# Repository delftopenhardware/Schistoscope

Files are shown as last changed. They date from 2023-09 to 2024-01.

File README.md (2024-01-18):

# Schistoscope
TU Delft Open Hardware Schistoscope

Navigate to 'Assembly Guide' or https://delftopenhardware.github.io/SchistoscopeDocs/ to see how to build the scope

All the parts CAD parts are located in the 'CAD' folder

The BOM can be found in the 'BOM' folder    



This project is a part of the Inspired  
https://inspired-diagnostics.info/

## Reference 
Oyibo, P., Jujjavarapu, S., Meulah, B., Agbana, T., Braakman, I., Van Diepen, A., Bengtson, M., Van Lieshout, L., Oyibo, W., Vdovine, G., & Diehl, J. C. (2022). Schistoscope: An Automated Microscope with Artificial Intelligence for Detection of Schistosoma haematobium Eggs in Resource-Limited Settings. Micromachines, 13(5), 643. https://doi.org/10.3390/mi13050643

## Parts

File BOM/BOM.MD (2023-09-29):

| Item # | Name | Specs. | Qty. | Price per piece (€) | Shipping (€) | Total   per Schistoscope (€) |  | Total cost (€) |  €    799,23  | Link |  |  |
|---|---|---|---|---|---|---|---|---|---|---|---|---|
| Motors   and drivers |  |   |   |   |   |   |   |   |   |   |  |  |
| 1 | Stepper motor | NEMA 11, 1 mm pitch, 50 mm | 2 |  €                     24,59  |  €         24,20  |  €                                   73,38  |   |   |   | https://nl.aliexpress.com/item/1005005533260185.html?spm=a2g0o.productlist.main.21.d7193af5nTc0bL&algo_pvid=0311f4ec-5321-4d68-99e3-2e47c6b58b74&algo_exp_id=0311f4ec-5321-4d68-99e3-2e47c6b58b74-10&pdp_npi=4%40dis%21EUR%2136.33%2135.24%21%21%2138.24%21%21%40211b88ef16938677846513431e329a%2112000033439717476%21sea%21NL%210%21A&curPageLogUid=17Ds95Ps0tr9 |  |  |
| 2 | Stepper motor | NEMA 11, 1 mm pitch, 100 mm | 1 |  €                     25,10  |  €           5,61  |  €                                   30,71  |   |   |   | https://nl.aliexpress.com/item/1005005533260185.html?spm=a2g0o.productlist.main.21.d7193af5nTc0bL&algo_pvid=0311f4ec-5321-4d68-99e3-2e47c6b58b74&algo_exp_id=0311f4ec-5321-4d68-99e3-2e47c6b58b74-10&pdp_npi=4%40dis%21EUR%2136.33%2135.24%21%21%2138.24%21%21%40211b88ef16938677846513431e329a%2112000033439717476%21sea%21NL%210%21A&curPageLogUid=17Ds95Ps0tr9 |  |  |
| 3 | Stepper motor driver | DRV8825 + heatsink | 3 |  €                       1,05  |  €           1,55  |  €                                     4,70  |   |   |   | https://nl.aliexpress.com/item/1005001621676770.html?spm=a2g0o.productlist.main.45.7d113e71c5rpfz&algo_pvid=0ba04a30-e339-455d-b8e5-7db9d5e80bba&algo_exp_id=0ba04a30-e339-455d-b8e5-7db9d5e80bba-22&pdp_npi=4%40dis%21EUR%210.91%210.73%21%21%210.96%21%21%40211b88ee16938682042218596e4ee1%2112000020026811115%21sea%21NL%210%21A&curPageLogUid=FATsjuqZyCN2 |  |  |
|  |   |  |   |  |   |  |  |  |  |  |  |  |
| Structural   components |  |   |   |   |   |   |   |   |   |   |  |  |
| 5 | Aluminum profile | 20x20x350 mm | 2 |  €                       6,11  |  €           1,74  |  €                                   13,96  |   |   |   | https://nl.aliexpress.com/item/1005002537611699.html?spm=a2g0o.productlist.main.3.4a031ab0olaA8Y&algo_pvid=1cb8bec3-2328-4782-988c-cffaef372e91&algo_exp_id=1cb8bec3-2328-4782-988c-cffaef372e91-1&pdp_npi=4%40dis%21EUR%217.49%215.98%21%21%217.88%21%21%40211b88f016938699631611766e6877%2112000021048744254%21sea%21NL%210%21A&curPageLogUid=FJZzS7E2CY5k |  |  |
| 6 | Aluminum profile | 40x20x300 mm | 1 |  €                     11,87  |  €                -    |  €                                   11,87  |   |   |   | https://nl.aliexpress.com/item/1005002453496457.html?spm=a2g0o.productlist.main.51.1df46917MQxx1B&algo_pvid=2cc73904-420a-4249-9133-c5c1c338129d&algo_exp_id=2cc73904-420a-4249-9133-c5c1c338129d-25&pdp_npi=4%40dis%21EUR%2119.64%2119.64%21%21%2120.67%21%21%4021038eda16938702597077618e5c7a%2112000020710616520%21sea%21NL%210%21A&curPageLogUid=VMwzInqvGpVO |  |  |
| 7 | Aluminum profile | 20x20x300 mm | 3 |  €                       7,28  |  €           1,74  |  €                                   23,58  |   |   |   | https://nl.aliexpress.com/item/1005002537611699.html?spm=a2g0o.productlist.main.3.4a031ab0olaA8Y&algo_pvid=1cb8bec3-2328-4782-988c-cffaef372e91&algo_exp_id=1cb8bec3-2328-4782-988c-cffaef372e91-1&pdp_npi=4%40dis%21EUR%217.49%215.98%21%21%217.88%21%21%40211b88f016938699631611766e6877%2112000021048744254%21sea%21NL%210%21A&curPageLogUid=FJZzS7E2CY5k |  |  |
| 8 | Aluminum profile | 20x20x215 mm | 2 |  €                       8,46  |  €           1,74  |  €                                   18,66  |   |   |   | https://nl.aliexpress.com/item/1005002537611699.html?spm=a2g0o.productlist.main.3.4a031ab0olaA8Y&algo_pvid=1cb8bec3-2328-4782-988c-cffaef372e91&algo_exp_id=1cb8bec3-2328-4782-988c-cffaef372e91-1&pdp_npi=4%40dis%21EUR%217.49%215.98%21%21%217.88%21%21%40211b88f016938699631611766e6877%2112000021048744254%21sea%21NL%210%21A&curPageLogUid=FJZzS7E2CY5k |  |  |
| 9 | Aluminum profile | 20x20x200 mm | 2 |  €                       7,63  |  €           1,74  |  €                                   17,00  |   |   |   | https://nl.aliexpress.com/item/1005002537611699.html?spm=a2g0o.productlist.main.3.4a031ab0olaA8Y&algo_pvid=1cb8bec3-2328-4782-988c-cffaef372e91&algo_exp_id=1cb8bec3-2328-4782-988c-cffaef372e91-1&pdp_npi=4%40dis%21EUR%217.49%215.98%21%21%217.88%21%21%40211b88f016938699631611766e6877%2112000021048744254%21sea%21NL%210%21A&curPageLogUid=FJZzS7E2CY5k |  |  |
| 10 | Aluminum profile | 20x20x175 mm | 2 |  €                       7,63  |  €           1,74  |  €                                   17,00  |   |   |   | https://nl.aliexpress.com/item/1005002537611699.html?spm=a2g0o.productlist.main.3.4a031ab0olaA8Y&algo_pvid=1cb8bec3-2328-4782-988c-cffaef372e91&algo_exp_id=1cb8bec3-2328-4782-988c-cffaef372e91-1&pdp_npi=4%40dis%21EUR%217.49%215.98%21%21%217.88%21%21%40211b88f016938699631611766e6877%2112000021048744254%21sea%21NL%210%21A&curPageLogUid=FJZzS7E2CY5k |  |  |
| 11 | Corner brackets |   | 16 |  €                       6,46  |  €                -    |  €                                     6,46  |   |   |   | https://nl.aliexpress.com/item/4000063076132.html?spm=a2g0o.productlist.main.25.7da814435etbcl&algo_pvid=19aa6fcc-ced3-47ff-abb9-b12fac77b6bf&algo_exp_id=19aa6fcc-ced3-47ff-abb9-b12fac77b6bf-12&pdp_npi=4%40dis%21EUR%2112.20%216.46%21%21%2112.80%21%21%40211b615316947241743964861eaa47%2110000000161993707%21sea%21NL%210%21AS&curPageLogUid=rLXXE8yB8w6T |  |  |
| 12 | Rubber feet | M4 | 4 |  €                       3,68  |  €           4,96  |  €                                     8,64  |   |   |   | https://nl.aliexpress.com/item/1005003681572582.html?spm=a2g0o.productlist.main.25.5ca63b58zzCfgb&algo_pvid=e28b779e-7411-432f-84bb-55b8b368539a&algo_exp_id=e28b779e-7411-432f-84bb-55b8b368539a-12&pdp_npi=4%40dis%21EUR%214.71%214.61%21%21%214.94%21%21%40211b615316947243129446972eaa47%2112000026782305036%21sea%21NL%210%21AS&curPageLogUid=B0LszgvKN7rm |  |  |
| 13 | Spring | M5*15 mm | 4 |  €                       0,43  |  €           1,37  |  €                                     3,07  |   |   |   | https://nl.aliexpress.com/item/1005005974742507.html?spm=a2g0o.productlist.main.45.7bac5dd5iFG5OJ&algo_pvid=2046b9d0-bc3c-4736-8237-c5244236c177&algo_exp_id=2046b9d0-bc3c-4736-8237-c5244236c177-22&pdp_npi=4%40dis%21EUR%212.12%211.7%21%21%2116.27%21%21%40211b617a16939507018131128e6a33%2112000035130817674%21sea%21NL%210%21A&curPageLogUid=S3SDvNti9Aof |  |  |
| 14 | Hinge |  | 2 |  €                       0,23  |  €                -    |  €                                     0,46  |  |  |  | https://nl.aliexpress.com/item/32953581270.html?spm=a2g0o.productlist.main.5.6b3668aaplRnSN&algo_pvid=2c0c1b08-6c85-4129-bd1b-7743bc25a72d&algo_exp_id=2c0c1b08-6c85-4129-bd1b-7743bc25a72d-2&pdp_npi=4%40dis%21EUR%212.94%210.46%21%21%213.10%21%21%40211b617a16939508408492869e6a33%2166382201404%21sea%21NL%210%21A&curPageLogUid=eFfJ6r2JXGj9 |  |  |
| 15 | Lock plate |  | 1 |  €                       0,46  |  €                -    |  €                                     0,46  |  |  |  | https://nl.aliexpress.com/item/32933924674.html?spm=a2g0o.productlist.main.3.412c3931eQBrTb&algo_pvid=9e3379fe-aa2c-4b70-85b0-87a244084bad&algo_exp_id=9e3379fe-aa2c-4b70-85b0-87a244084bad-1&pdp_npi=4%40dis%21EUR%210.70%210.46%21%21%210.74%21%21%40211b617a16939509787254501e6a33%2166224476012%21sea%21NL%210%21A&curPageLogUid=FMX9X8mry7T9 |  |  |
|  |   |  |   |  |   |  |  |  |  |  |  |  |
| Mechanical   fasteners |  |   |   |   |   |   |   |   |   |   |  |  |
| 16 | Bolt | M2*6 mm | 8 |  €                       1,84  |  €                -    |  €                                     1,84  |   |   |   | https://nl.aliexpress.com/item/1005004833515587.html?spm=a2g0o.productlist.main.7.107a4abed7Lp4O&algo_pvid=4e5c6b8d-3b2b-4882-8919-a36d85c2f3a4&algo_exp_id=4e5c6b8d-3b2b-4882-8919-a36d85c2f3a4-3&pdp_npi=4%40dis%21EUR%2113.46%211.84%21%21%2114.12%21%21%40211b88f116947270870846250efcfc%2112000030659841609%21sea%21NL%210%21AS&curPageLogUid=aU9x01JDrid9 |  |  |
| 17 | Bolt | M2*8 mm | 12 |  |  |  |   |   |   |  |  |  |
| 18 | Bolt  | M2*10 mm | 8 |  |  |  |   |   |   |  |  |  |
| 19 | Bolt | M2*16 mm | 2 |  |  |  |   |   |   |  |  |  |
| 20 | Bolt | M3*6 mm | 2 |  €                       5,75  |  €                -    |  €                                     5,75  |  |  |  | https://nl.aliexpress.com/item/1005004833515587.html?spm=a2g0o.productlist.main.7.107a4abed7Lp4O&algo_pvid=4e5c6b8d-3b2b-4882-8919-a36d85c2f3a4&algo_exp_id=4e5c6b8d-3b2b-4882-8919-a36d85c2f3a4-3&pdp_npi=4%40dis%21EUR%2113.46%211.84%21%21%2114.12%21%21%40211b88f116947270870846250efcfc%2112000030659841609%21sea%21NL%210%21AS&curPageLogUid=aU9x01JDrid9 |  |  |
| 21 | Bolt | M3*8 mm | 19 |  |  |  |  |  |  |  |  |  |
| 22 | Bolt | M3*12 mm | 10 |  |  |  |  |  |  |  |  |  |
| 23 | Bolt | M3*16 mm \| countersunk | 12 |  |  |  |  |  |  |  |  |  |
| 24 | Bolt | M3*20 mm | 4 |  |  |  |  |  |  |  |  |  |
| 25 | Bolt | M4*8 mm | 98 |  €                       6,29  |  €                -    |  €                                     6,29  |  |  |  | https://nl.aliexpress.com/item/32879751148.html?spm=a2g0o.productlist.main.83.b89572a1z7If2W&algo_pvid=83133542-d8ce-405e-b2ad-da25d44a70e7&algo_exp_id=83133542-d8ce-405e-b2ad-da25d44a70e7-41&pdp_npi=4%40dis%21EUR%216.93%216.86%21%21%217.27%21%21%4021038eda16947280350625746e14c3%2165522335530%21sea%21NL%210%21AS&curPageLogUid=AfVsvWcOz8tB |  |  |
| 26 | Bolt | M4*12 mm | 4 |  €                       6,48  |  €                -    |  €                                     6,48  |  |  |  | https://nl.aliexpress.com/item/1005004129378778.html?spm=a2g0o.productlist.main.67.565d590atXPBRa&algo_pvid=966ad033-4291-4696-85c4-f2033d81a041&algo_exp_id=966ad033-4291-4696-85c4-f2033d81a041-33&pdp_npi=4%40dis%21EUR%2112.58%213.99%21%21%2113.19%21%21%4021038eda16947278400843976e14c3%2112000028131816313%21sea%21NL%210%21AS&curPageLogUid=WjhHm1uIKRo7 |  |  |
| 27 | Bolt  | M4*24 mm | 2 |  |  |  |  |  |  |  |  |  |
| 28 | Bolt | M4*60 mm | 3 |  €                       8,81  |  €                -    |  €                                     8,81  |  |  |  | https://nl.aliexpress.com/item/1005006034026066.html?spm=a2g0o.productlist.main.21.50886603JV22ri&algo_pvid=5ac0b68b-b2eb-4c67-9b40-9e0facd0099b&algo_exp_id=5ac0b68b-b2eb-4c67-9b40-9e0facd0099b-10&pdp_npi=4%40dis%21EUR%218.59%218.59%21%21%2165.51%21%21%4021038eda16947276262111658e14c3%2112000035416757399%21sea%21NL%210%21AS&curPageLogUid=zP4y8BI3SNzx |  |  |
| 29 | Nut | M2 | 18 |  €                       2,33  |  €                -    |  €                                     2,33  |  |  |  | https://nl.aliexpress.com/item/32801603379.html?spm=a2g0o.productlist.main.7.318c5b32FxGWyW&algo_pvid=49a7c5f5-db01-4161-a6e3-d5bc8f2d427f&algo_exp_id=49a7c5f5-db01-4161-a6e3-d5bc8f2d427f-3&pdp_npi=4%40dis%21EUR%212.58%212.33%21%21%212.71%21%21%4021038eda16947273657776461e14c3%2112000015896626648%21sea%21NL%210%21AS&curPageLogUid=b00TKkob6eAL |  |  |
| 30 | Nut | M3  | 11 |  €                       1,16  |  €                -    |  €                                     1,16  |  |  |  | https://nl.aliexpress.com/item/32801603379.html?spm=a2g0o.productlist.main.7.318c5b32FxGWyW&algo_pvid=49a7c5f5-db01-4161-a6e3-d5bc8f2d427f&algo_exp_id=49a7c5f5-db01-4161-a6e3-d5bc8f2d427f-3&pdp_npi=4%40dis%21EUR%212.58%212.33%21%21%212.71%21%21%4021038eda16947273657776461e14c3%2112000015896626648%21sea%21NL%210%21AS&curPageLogUid=b00TKkob6eAL |  |  |
| 31 | Nut | M4 | 13 |  €                       2,33  |  €                -    |  €                                     2,33  |  |  |  | https://nl.aliexpress.com/item/32801603379.html?spm=a2g0o.productlist.main.7.318c5b32FxGWyW&algo_pvid=49a7c5f5-db01-4161-a6e3-d5bc8f2d427f&algo_exp_id=49a7c5f5-db01-4161-a6e3-d5bc8f2d427f-3&pdp_npi=4%40dis%21EUR%212.58%212.33%21%21%212.71%21%21%4021038eda16947273657776461e14c3%2112000015896626648%21sea%21NL%210%21AS&curPageLogUid=b00TKkob6eAL |  |  |
| 32 | Ring | M3 | 9 |  €                       0,47  |  €                -    |  €                                     4,23  |  |  |  | https://nl.aliexpress.com/item/1005003352791998.html?spm=a2g0o.productlist.main.11.720b1476JZjMVn&algo_pvid=a07a7e7d-cea3-4dfc-982f-57bffc4d86cd&algo_exp_id=a07a7e7d-cea3-4dfc-982f-57bffc4d86cd-5&pdp_npi=4%40dis%21EUR%211.89%210.47%21%21%211.98%21%21%4021038eda16947274846798291e14c3%2112000025362131584%21sea%21NL%210%21AS&curPageLogUid=0l3BEowbRJAW |  |  |
| 33 | Sliding nut  | M3 | 2 |  €                       0,48  |  €                -    |  €                                     0,96  |  |  |  | https://nl.aliexpress.com/item/32814359094.html?spm=a2g0o.productlist.main.1.71a75b4bs55PPO&algo_pvid=3670bd18-bf23-4e76-b2d3-dc5f92dc157a&algo_exp_id=3670bd18-bf23-4e76-b2d3-dc5f92dc157a-0&pdp_npi=4%40dis%21EUR%213.18%210.47%21%21%213.34%21%21%4021038eda16947275404078740e14c3%2166498695474%21sea%21NL%210%21AS&curPageLogUid=C1P3e9JiY4ac |  |  |
| 34 | Sliding nut | M4 | 102 |  €                       1,91  |  €                -    |  €                                     1,91  |  |  |  | https://nl.aliexpress.com/item/32814359094.html?spm=a2g0o.productlist.main.1.71a75b4bs55PPO&algo_pvid=3670bd18-bf23-4e76-b2d3-dc5f92dc157a&algo_exp_id=3670bd18-bf23-4e76-b2d3-dc5f92dc157a-0&pdp_npi=4%40dis%21EUR%213.18%210.47%21%21%213.34%21%21%4021038eda16947275404078740e14c3%2166498695474%21sea%21NL%210%21AS&curPageLogUid=C1P3e9JiY4ac |  |  |
| 35 | Spacers | M2*5 mm | 2 |  €                       0,23  |  €                -    |  €                                     0,46  |  |  |  | https://nl.aliexpress.com/item/32862529967.html?spm=a2g0o.productlist.main.1.8cea41a0LRbWb3&algo_pvid=894c3a99-79f5-4bdf-a29a-43573f16a81b&algo_exp_id=894c3a99-79f5-4bdf-a29a-43573f16a81b-0&pdp_npi=4%40dis%21EUR%214.19%210.46%21%21%214.42%21%21%40211b617a16939510482205215e6a33%2110000000197494051%21sea%21NL%210%21A&curPageLogUid=GCXrXbsGFC2N |  |  |
| 36 | Spacers | M2*10 mm | 4 |  |  |  |  |  |  |  |  |  |
| 37 | Spacers | M2*15 mm | 4 |  |  |  |  |  |  |  |  |  |
| 38 | Melt insert | M2 | 12 |  €                       1,12  |  €           1,81  |  €                                     2,93  |  |  |  | https://nl.aliexpress.com/item/1005003452619683.html?spm=a2g0o.order_list.order_list_main.4.53e379d2cTGRcJ&gatewayAdapt=glo2nld |  |  |
| 39 | Melt insert | M3 | 14 |  €                       1,12  |  €           1,81  |  €                                     2,93  |  |  |  | https://nl.aliexpress.com/item/1005003452619683.html?spm=a2g0o.order_list.order_list_main.4.53e379d2cTGRcJ&gatewayAdapt=glo2nld |  |  |
|  |   |  |   |  |   |  |  |  |  |  |  |  |
| Optics |   |   |   |   |   |   |   |   |   |   |  |  |
| 40 | Condenser lenses |  | 2 |  €                     23,17  |  €         10,98  |  €                                   57,32  |  |  |  | https://www.thorlabs.com/thorproduct.cfm?partnumber=ACL2520U-DG15 |  |  |
| 41 | Thorlabs C mount |  | 1 |  €                     31,91  |  €         10,98  |  €                                   42,89  |  |  |  | https://www.thorlabs.com/thorproduct.cfm?partnumber=CML50 |  |  |
| 42 | 50 mm spacer |  | 1 |  €                     21,25  |  €           8,89  |  €                                   30,14  |  |  |  | https://nl.aliexpress.com/item/32817786051.html?spm=a2g0o.order_list.order_list_main.424.3cbe79d2ZJ7jjH&gatewayAdapt=glo2nld |  |  |
| 43 | Objective | 4X | 1 |  €                     12,61  |  €           0,79  |  €                                   13,40  |  |  |  | https://nl.aliexpress.com/item/1005005745368395.html?spm=a2g0o.productlist.main.7.37df7d05hUo2kP&algo_pvid=9ba746bd-af66-4623-a81c-2cea46c86979&algo_exp_id=9ba746bd-af66-4623-a81c-2cea46c86979-3&pdp_npi=4%40dis%21EUR%2119.69%2112.61%21%21%2120.73%21%21%40211b88ee16938683627901977e4ee1%2112000034194058893%21sea%21NL%210%21A&curPageLogUid=8n2etXci26ZF |  |  |
|  |   |  |   |  |   |  |  |  |  |  |  |  |
| Housing |   |   |   |   |   |   |   |   |   |   |  |  |
| 44 | Backplate |  | 1 |  |   |  €                                            -    |  |  |  |  |  |  |
| 45 | Bottomplate |  | 1 |  |   |  €                                            -    |  |  |  |  |  |  |
| 46 | Light tower plate |  | 1 |  |   |  €                                            -    |  |  |  |  |  |  |
| 47 | Top plate |  | 1 |  |   |  €                                            -    |  |  |  |  |  |  |
| 48 | Front and side plate |  | 1 |  |   |  €                                            -    |  |  |  |  |  |  |
| 49 | Electronics plate |  | 1 |  |   |  €                                            -    |  |  |  |  |  |  |
| 50 | Window |  | 1 |  |   |  €                                            -    |  |  |  |  |  |  |
|  |   |  |   |  |   |  |  |  |  |  |  |  |
| 3D   printed parts |  | Printing time | Weight (kg) |   |   |   |   |   |   |   |  |  |
| 51 | Clamp | 3 h, 06 min | 0,033 |  €                     25,61  |  €                -    |  €                                     0,85  |  |  |  |  |  |  |
| 52 | Clamp mount | 0 h, 56 min | 0,010 |  |  €                -    |  €                                     0,26  |  |  |  |  |  |  |
| 53 | Light tower \| Bottom | 0 h, 55 min | 0,008 |  |  €                -    |  €                                     0,20  |  |  |  |  |  |  |
| 54 | Light tower \| Spacer 1 | 0 h, 57 min | 0,009 |  |  €                -    |  €                                     0,23  |  |  |  |  |  |  |
| 55 | Light tower \| Spacer 2 | 1 h, 17 min | 0,012 |  |  €                -    |  €                                     0,31  |  |  |  |  |  |  |
| 56 | Light tower \| Top | 0 h, 26 min | 0,004 |  |  €                -    |  €                                     0,10  |  |  |  |  |  |  |
| 57 | Sample stage | 2h, 19 min | 0,025 |  |  €                -    |  €                                     0,64  |  |  |  |  |  |  |
| 58 | Sample stage holder | 5h, 57 min | 0,066 |  |  €                -    |  €                                     1,69  |  |  |  |  |  |  |
| 59 | XY-motor mount | 1h, 32 min | 0,017 |  |  €                -    |  €                                     0,44  |  |  |  |  |  |  |
| 60 | Z-motor mount | 2h, 16 min | 0,024 |  |  €                -    |  €                                     0,61  |  |  |  |  |  |  |
| 61 | X-endstop mount \| left | 0h, 20 min | 0,003 |  |  €                -    |  €                                     0,08  |  |  |  |  |  |  |
| 62 | X-endstop mount \| right | 0h, 20 min | 0,003 |  |  €                -    |  €                                     0,08  |  |  |  |  |  |  |
| 63 | Y-endstop mount \| front | 1h, 30 min | 0,014 |  |  €                -    |  €                                     0,36  |  |  |  |  |  |  |
| 64 | Y-endstop mount \| back | 1h, 23 min | 0,013 |  |  €                -    |  €                                     0,33  |  |  |  |  |  |  |
| 65 | Z-endstop mount \| top | 0h, 54 min | 0,008 |  |  €                -    |  €                                     0,20  |  |  |  |  |  |  |
| 66 | Z-endstop mount \| bottom | 0h, 54 min | 0,008 |  |  €                -    |  €                                     0,20  |  |  |  |  |  |  |
|  |   |  |   |  |   |  |  |  |  |  |  |  |
| Electronics |  |   |   |   |   |   |   |   |   |   |  |  |
| 67 | LED | 1 W \| Neutral white | 1 |  €                       0,48  |  €                -    |  €                                     0,48  |  |  |  | https://nl.aliexpress.com/item/32843112997.html?spm=a2g0o.productlist.main.3.5bae30f4uv6qmm&algo_pvid=4606b815-0664-4889-9872-287727966721&algo_exp_id=4606b815-0664-4889-9872-287727966721-1&pdp_npi=4%40dis%21EUR%211.11%210.48%21%21%211.17%21%21%40211b88ee16938684230222506e4ee1%2112000020788789290%21sea%21NL%210%21A&curPageLogUid=0nt5CjDd9UbP |  |  |
| 68 | LED heat sink |  | 1 |  €                       1,11  |  €           1,21  |  €                                     2,32  |  |  |  | https://nl.aliexpress.com/item/32946892914.html?spm=a2g0o.productlist.main.17.3b29dedd9LJrVg&algo_pvid=90072425-e634-436b-980e-15a2cabb4977&algo_exp_id=90072425-e634-436b-980e-15a2cabb4977-8&pdp_npi=4%40dis%21EUR%211.65%211.11%21%21%211.74%21%21%40211b88ee16938685274753614e4ee1%2166231330395%21sea%21NL%210%21A&curPageLogUid=omekcjr4qOcD |  |  |
| 69 | Raspberry Pi HQ camera |  | 1 |  €                     73,76  |  €                -    |  €                                   73,76  |  |  |  | https://nl.farnell.com/webapp/wcs/stores/servlet/AjaxOrderItemDisplayView?catalogId=15001&storeId=10168&langId=31&krypto=1AaN3Fc%2FAhIDjZK0aHhAXfAbzBE3qYfibJ1o9HOy%2BMn4tqEfTGiNbnEG4gbrvMUznPGuxycQuTqdZSr9gFm9YvDxznP4D7WW7tD2Aslp%2BV87YiYQaJn9uaQhQMJK4MryaxIpwX1Mxk6epYt0gGzPgMclI24hfyT90Cb%2FRy7Kh%2FiqdY0mKM2HtqNxbVpXr6PB&ddkey=https%3AOrderCalculate |  |  |
| 70 | Raspberry Pi Pico |  | 1 |  €                       1,23  |  €           1,23  |  €                                     2,46  |  |  |  | https://nl.aliexpress.com/item/1005005793264636.html?pdp_npi=2%40dis%21EUR%21%E2%82%AC2%2C46%21%E2%82%AC1%2C23%21%21%21%21%21%40211b5e2b16938688945022418e9ea7%2112000034373780385%21btf&_t=pvid%3A7ec7a95a-5d26-46b4-8dae-ac2173346fff&spm=a2g0o.ppclist.product.mainProduct&gatewayAdapt=glo2nld |  |  |
| 71 | Male header pins | 1x20 | 2 |  €                       0,23  |  €                -    |  €                                     0,46  |  |  |  | https://nl.aliexpress.com/item/1005003541838313.html?spm=a2g0o.productlist.main.5.38657920UHiFfj&algo_pvid=b91a0dc9-cde7-4e87-be01-32611e120474&algo_exp_id=b91a0dc9-cde7-4e87-be01-32611e120474-2&pdp_npi=4%40dis%21EUR%211.19%210.47%21%21%211.25%21%21%40211b5e1f16938689381143392ef835%2112000026227195343%21sea%21NL%210%21A&curPageLogUid=Wy3E9NlF7Oyk |  |  |
| 72 | Female header pins | 1x20 | 2 |  €                       0,71  |  €           0,64  |  €                                     2,06  |  |  |  | https://nl.aliexpress.com/item/4001198421663.html?spm=a2g0o.productlist.main.13.5d9c11f8RKH5Dq&algo_pvid=0a1ae0be-8849-4267-be57-d02ba814f51b&algo_exp_id=0a1ae0be-8849-4267-be57-d02ba814f51b-6&pdp_npi=4%40dis%21EUR%211.43%211.22%21%21%211.51%21%21%40211b5e1f16938690094344191ef835%2110000015275671653%21sea%21NL%210%21A&curPageLogUid=zlZkDgDlPU4f |  |  |
| 73 | Female header pins | 1x8 | 6 |  €                       0,85  |  €           0,64  |  €                                     5,74  |  |  |  | https://nl.aliexpress.com/item/4001198421663.html?spm=a2g0o.productlist.main.13.5d9c11f8RKH5Dq&algo_pvid=0a1ae0be-8849-4267-be57-d02ba814f51b&algo_exp_id=0a1ae0be-8849-4267-be57-d02ba814f51b-6&pdp_npi=4%40dis%21EUR%211.43%211.22%21%21%211.51%21%21%40211b5e1f16938690094344191ef835%2110000015275671653%21sea%21NL%210%21A&curPageLogUid=zlZkDgDlPU4f |  |  |
| 74 | Custom PCB |  | 1 |  |   |  €                                            -    |  |  |  |  |  |  |
| 75 | Capacitor | 100 uF | 3 |  €                       1,28  |  €           1,12  |  €                                     4,96  |  |  |  | https://nl.aliexpress.com/item/33049456328.html?spm=a2g0o.productlist.main.11.424c7bc0WmZY7r&algo_pvid=50022565-d7b9-4c7f-b951-e04761278538&algo_exp_id=50022565-d7b9-4c7f-b951-e04761278538-5&pdp_npi=4%40dis%21EUR%210.63%210.54%21%21%214.85%21%21%40211b5e1f16938691137125431ef835%2167436126751%21sea%21NL%210%21A&curPageLogUid=6ku2GSQKeznm |  |  |
| 76 | MOSFET module | 15A, 400W | 1 |  €                       0,43  |  €           0,91  |  €                                     1,34  |  |  |  | https://nl.aliexpress.com/item/32803005422.html?spm=a2g0o.productlist.main.1.3e397860t4cqJR&algo_pvid=0d3bf6ce-72ba-4bb5-8b94-153125c620c6&algo_exp_id=0d3bf6ce-72ba-4bb5-8b94-153125c620c6-0&pdp_npi=4%40dis%21EUR%210.48%210.43%21%21%210.51%21%21%40211b5e1f16938692423487198ef835%2164323132051%21sea%21NL%210%21A&curPageLogUid=NExKTzmhwzbe |  |  |
| 77 | Power supply | RPD-60A | 1 |  €                     22,63  |  €                -    |  €                                   22,63  |  |  |  | https://nl.farnell.com/mean-well/rpd-60a/power-supply-medical-ac-dc-2-o/dp/2815574?gclid=EAIaIQobChMI6YjvqYuSgQMVSq53Ch0gQQQ6EAAYAiAAEgJECPD_BwE&mckv=s_dc\|pcrid\|530720719616\|kword\|rpd%2060a\|match\|p\|plid\|\|slid\|\|product\|\|pgrid\|126927693809\|ptaid\|kwd-382918195196\|&CMP=KNC-GNL-GEN-SKU-MDC-PS_Software_TT_OE_LED-Test-985 |  |  |
| 78 | Raspberry Pi 3/4 |  | 1 |  €                     32,18  |  €                -    |  €                                   32,18  |  |  |  | https://nl.farnell.com/raspberry-pi/raspberrypi-modb-1gb/raspberry-pi-3-model-b/dp/2525225?src=raspberrypi |  |  |
| 79 | SD card | Silicon Power NAND | 1 |  €                       5,49  |  €                -    |  €                                     5,49  |  |  |  | https://www.amazon.nl/Silicon-Power-FBE-SU032GBSTHBU1V1GEU-geheugenkaart-32/dp/B07RMXNLF4/ref=sr_1_5?crid=3PLZIA4J3DZNX&keywords=silicon%2Bpower%2B3d%2Bnand&qid=1694724865&sprefix=silicon%2Bpower%2B%2Caps%2C126&sr=8-5&th=1 |  |  |
| 80 | Ventilator kit | for Raspberry Pi 3/4 | 1 |  €                       4,54  |  €           5,66  |  €                                   10,20  |  |  |  | https://nl.aliexpress.com/item/1005005584107979.html?spm=a2g0o.productlist.main.43.4bb729e2hnT2rD&algo_pvid=4ef9b156-4916-4a35-bfe7-5277a10c1f49&algo_exp_id=4ef9b156-4916-4a35-bfe7-5277a10c1f49-21&pdp_npi=4%40dis%21EUR%214.17%213.75%21%21%2131.93%21%21%40211b88f016938695408355702e6877%2112000033644457997%21sea%21NL%210%21A&curPageLogUid=OmJkXpY4bIcm |  |  |
| 81 | TPU | Google Coral | 2 |  €                     56,60  |  €                -    |  €                                113,20  |  |  |  | https://nl.farnell.com/pi3g/g950-01456-01/usb-accelerator-raspberry-pi/dp/3583033?st=coral |  |  |
| 82 | Rocker switch | 33x25 mm | 1 |  €                       1,12  |  €           0,58  |  €                                     1,70  |  |  |  | https://nl.aliexpress.com/item/1005001694446039.html?spm=a2g0o.productlist.main.43.667641abRmolE5&algo_pvid=b540751c-e72a-4ac2-97e6-2e523baead3a&algo_exp_id=b540751c-e72a-4ac2-97e6-2e523baead3a-21&pdp_npi=4%40dis%21EUR%211.73%211.12%21%21%211.82%21%21%40211b88f016938696934687339e6877%2112000018105924879%21sea%21NL%210%21A&curPageLogUid=d1r71NCegAr7 |  |  |
| 83 | Power socket | 3 pin | 1 |  €                       0,69  |  €           2,69  |  €                                     3,38  |  |  |  | https://nl.aliexpress.com/item/4000380736505.html?spm=a2g0o.order_list.order_list_main.436.3ba579d2aSoXNa&gatewayAdapt=glo2nld |  |  |
| 84 | End switch |  | 6 |  €                       2,21  |  €                -    |  €                                     2,21  |  |  |  | https://nl.aliexpress.com/item/32939882024.html?spm=a2g0o.order_list.order_list_main.57.3cbe79d2jAamDa&gatewayAdapt=glo2nld |  |  |
|  |   |  |   |  |   |  |  |  |  |  |  |  |
| Wires   and connectors |  |   |   |   |   |   |   |   |   |   |  |  |
| 85 | Wire | 22 AWG \| 550 mm | 2 |  €                       0,47  |  €                -    |  €                                     0,94  |  |  |  | https://nl.aliexpress.com/item/1005004750475982.html?spm=a2g0o.productlist.main.15.33c626d9QHVmUn&algo_pvid=e456ecd9-aba0-493f-9c6c-09f29dba53b9&algo_exp_id=e456ecd9-aba0-493f-9c6c-09f29dba53b9-7&pdp_npi=4%40dis%21EUR%214.10%210.47%21%21%214.32%21%21%40211b88ee16938711022977528e4ee0%2112000030335587229%21sea%21NL%210%21A&curPageLogUid=rVN2Luqel4s8 |  |  |
| 86 | Wire | 22 AWG \| 400 mm | 1 |  |  |  |  |  |  |  |  |  |
| 87 | Wire | 22 AWG \| 300 mm | 4 |  |  |  |  |  |  |  |  |  |
| 88 | Wire | 22 AWG \| 250 mm | 1 |  |  |  |  |  |  |  |  |  |
| 89 | Wire | 22 AWG \| 200 mm | 4 |  |  |  |  |  |  |  |  |  |
| 90 | Wire | 22 AWG \| 120 mm | 2 |  |  |  |  |  |  |  |  |  |
| 91 | Wire | 22 AWG \| 100 mm | 1 |  |  |  |  |  |  |  |  |  |
| 92 | Wire | 10 AWG \| 500 mm | 2 |  €                       3,28  |  €                -    |  €                                     6,56  |  |  |  | https://nl.aliexpress.com/item/1005004750475982.html?spm=a2g0o.productlist.main.15.33c626d9QHVmUn&algo_pvid=e456ecd9-aba0-493f-9c6c-09f29dba53b9&algo_exp_id=e456ecd9-aba0-493f-9c6c-09f29dba53b9-7&pdp_npi=4%40dis%21EUR%214.10%210.47%21%21%214.32%21%21%40211b88ee16938711022977528e4ee0%2112000030335587229%21sea%21NL%210%21A&curPageLogUid=rVN2Luqel4s8 |  |  |
| 93 | Wire | 10 AWG \| 350 mm | 1 |  |  |  |  |  |  |  |  |  |
| 94 | Wire | 10 AWG \| 150 mm | 2 |  |  |  |  |  |  |  |  |  |
| 95 | JST connector | XH \| female  | 20 |  €                       0,91  |  €           0,45  |  €                                     1,36  |  |  |  | https://nl.aliexpress.com/item/1005004300032921.html?spm=a2g0o.productlist.main.7.2de4185fYU0pdt&algo_pvid=c988d294-ba9f-470b-b6c0-00092072a071&algo_exp_id=c988d294-ba9f-470b-b6c0-00092072a071-3&pdp_npi=4%40dis%21EUR%212.97%211.9%21%21%213.11%21%21%40211b5db216947249509028695e768d%2112000028678908419%21sea%21NL%210%21AS&curPageLogUid=qhjVsdfWx3AP |  |  |
| 96 | JST plug | XH2P \| female | 3 |  €                       0,61  |  €           0,45  |  €                                     2,28  |  |  |  | https://nl.aliexpress.com/item/1005004300032921.html?spm=a2g0o.productlist.main.7.2de4185fYU0pdt&algo_pvid=c988d294-ba9f-470b-b6c0-00092072a071&algo_exp_id=c988d294-ba9f-470b-b6c0-00092072a071-3&pdp_npi=4%40dis%21EUR%212.97%211.9%21%21%213.11%21%21%40211b5db216947249509028695e768d%2112000028678908419%21sea%21NL%210%21AS&curPageLogUid=qhjVsdfWx3AP |  |  |
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

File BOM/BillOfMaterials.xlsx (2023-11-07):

 | Item # | Name | Specs. | Qty. | Price per piece (€) | Shipping (€) | Total per Schistoscope (€) | Total cost (€) | €799.23 | Link
 | Motors and drivers
 | 1 | Stepper motor | NEMA 11, 1 mm pitch, 50 mm | 2 | €24.59 | €24.20 | €73.38 |  |  | https://nl.aliexpress.com/item/1005005533260185.html?curPageLogUid=17Ds95Ps0tr9
 | 2 | Stepper motor | NEMA 11, 1 mm pitch, 100 mm | 1 | €25.10 | €5.61 | €30.71 |  |  | https://nl.aliexpress.com/item/1005005533260185.html?curPageLogUid=17Ds95Ps0tr9
DRV and TMC | 3 | Stepper motor driver | DRV8825 + heatsink | 3 | €1.05 | €1.55 | €4.70 |  |  | https://nl.aliexpress.com/item/1005001621676770.html?curPageLogUid=FATsjuqZyCN2
 | Structural components
 | 5 | Aluminum profile | 20x20x350 mm | 2 | €6.11 | €1.74 | €13.96 |  |  | https://nl.aliexpress.com/item/1005002537611699.html?curPageLogUid=FJZzS7E2CY5k
 | 6 | Aluminum profile | 40x20x300 mm | 1 | €11.87 | €0.00 | €11.87 |  |  | https://nl.aliexpress.com/item/1005002453496457.html?curPageLogUid=VMwzInqvGpVO
 | 7 | Aluminum profile | 20x20x300 mm | 3 | €7.28 | €1.74 | €23.58 |  |  | https://nl.aliexpress.com/item/1005002537611699.html?curPageLogUid=FJZzS7E2CY5k
Bought 250 | 8 | Aluminum profile | 20x20x215 mm | 2 | €8.46 | €1.74 | €18.66 |  |  | https://nl.aliexpress.com/item/1005002537611699.html?curPageLogUid=FJZzS7E2CY5k
 | 9 | Aluminum profile | 20x20x200 mm | 2 | €7.63 | €1.74 | €17.00 |  |  | https://nl.aliexpress.com/item/1005002537611699.html?curPageLogUid=FJZzS7E2CY5k
Bought 250 | 10 | Aluminum profile | 20x20x175 mm | 2 | €7.63 | €1.74 | €17.00 |  |  | https://nl.aliexpress.com/item/1005002537611699.html?curPageLogUid=FJZzS7E2CY5k
Set of 50 | 11 | Corner brackets |  | 16 | €6.46 | €0.00 | €6.46 |  |  | https://nl.aliexpress.com/item/4000063076132.html?curPageLogUid=rLXXE8yB8w6T
Different | 12 | Rubber feet | M4 | 4 | €3.68 | €4.96 | €8.64 |  |  | https://nl.aliexpress.com/item/1005003681572582.html?curPageLogUid=B0LszgvKN7rm
10 set | 13 | Spring | M5*15 mm | 4 | €0.42 | €1.37 | €3.07 |  |  | https://nl.aliexpress.com/item/1005005974742507.html?curPageLogUid=S3SDvNti9Aof
12 Set Size unknown | 14 | Hinge |  | 2 | €0.23 | €0.00 | €0.46 |  |  | https://nl.aliexpress.com/item/32953581270.html?curPageLogUid=eFfJ6r2JXGj9
Medium | 15 | Lock plate |  | 1 | €0.46 | €0.00 | €0.46 |  |  | https://nl.aliexpress.com/item/32933924674.html?curPageLogUid=FMX9X8mry7T9
 | Mechanical fasteners
Bought Set | 16 | Bolt | M2*6 mm | 8 | €1.84 | €0.00 | €1.84 |  |  | https://nl.aliexpress.com/item/1005004833515587.html?curPageLogUid=aU9x01JDrid9
 | 17 | Bolt | M2*8 mm | 12
 | 18 | Bolt | M2*10 mm | 8
 | 19 | Bolt | M2*16 mm | 2
Bought set | 20 | Bolt | M3*6 mm | 2 | €5.75 | €0.00 | €5.75 |  |  | https://nl.aliexpress.com/item/1005004833515587.html?curPageLogUid=aU9x01JDrid9
 | 21 | Bolt | M3*8 mm | 19
 | 22 | Bolt | M3*12 mm | 10
 | 23 | Bolt | M3*16 mm | countersunk | 12
 | 24 | Bolt | M3*20 mm | 4
 | 25 | Bolt | M4*8 mm | 98 | €6.29 | €0.00 | €6.29 |  |  | https://nl.aliexpress.com/item/32879751148.html?curPageLogUid=AfVsvWcOz8tB
 | 26 | Bolt | M4*12 mm | 4 | €6.48 | €0.00 | €6.48 |  |  | https://nl.aliexpress.com/item/1005004129378778.html?curPageLogUid=WjhHm1uIKRo7
 | 27 | Bolt | M4*24 mm | 2
 | 28 | Bolt | M4*60 mm | 3 | €8.81 | €0.00 | €8.81 |  |  | https://nl.aliexpress.com/item/1005006034026066.html?curPageLogUid=zP4y8BI3SNzx
 | 29 | Nut | M2 | 18 | €2.33 | €0.00 | €2.33 |  |  | https://nl.aliexpress.com/item/32801603379.html?curPageLogUid=b00TKkob6eAL
 | 30 | Nut | M3 | 11 | €1.16 | €0.00 | €1.16 |  |  | https://nl.aliexpress.com/item/32801603379.html?curPageLogUid=b00TKkob6eAL
 | 31 | Nut | M4 | 13 | €2.33 | €0.00 | €2.33 |  |  | https://nl.aliexpress.com/item/32801603379.html?curPageLogUid=b00TKkob6eAL
 | 32 | Ring | M3 | 9 | €0.47 | €0.00 | €4.23 |  |  | https://nl.aliexpress.com/item/1005003352791998.html?curPageLogUid=0l3BEowbRJAW
 | 33 | Sliding nut | M3 | 2 | €0.48 | €0.00 | €0.96 |  |  | https://nl.aliexpress.com/item/32814359094.html?curPageLogUid=C1P3e9JiY4ac
 | 34 | Sliding nut | M4 | 102 | €1.91 | €0.00 | €1.91 |  |  | https://nl.aliexpress.com/item/32814359094.html?curPageLogUid=C1P3e9JiY4ac
 | 35 | Spacers | M2*5 mm | 2 | €0.23 | €0.00 | €0.46 |  |  | https://nl.aliexpress.com/item/32862529967.html?curPageLogUid=GCXrXbsGFC2N
 | 36 | Spacers | M2*10 mm | 4
 | 37 | Spacers | M2*15 mm | 4
OD4 L4 | 38 | Melt insert | M2 | 12 | €1.12 | €1.81 | €2.93 |  |  | https://nl.aliexpress.com/item/1005003452619683.html
OD5 L5 | 39 | Melt insert | M3 | 14 | €1.12 | €1.81 | €2.93 |  |  | https://nl.aliexpress.com/item/1005003452619683.html
M4 Missing
 | Optics
 | 40 | Condenser lenses |  | 2 | €23.17 | €10.98 | €57.32 |  |  | https://www.thorlabs.com/thorproduct.cfm?partnumber=ACL2520U-DG15
 | 41 | Thorlabs C mount |  | 1 | €31.91 | €10.98 | €42.89 |  |  | https://www.thorlabs.com/thorproduct.cfm?partnumber=CML50 | Scope has CML100(?)
 | 42 | 50 mm spacer |  | 1 | €21.25 | €8.89 | €30.14 |  |  | https://nl.aliexpress.com/item/32817786051.html
 | 43 | Objective | 4X | 1 | €12.61 | €0.79 | €13.40 |  |  | https://nl.aliexpress.com/item/1005005745368395.html?curPageLogUid=8n2etXci26ZF
 | Housing
 | 44 | Backplate |  | 1 |  |  | €0.00
 | 45 | Bottomplate |  | 1 |  |  | €0.00
 | 46 | Light tower plate |  | 1 |  |  | €0.00
 | 47 | Top plate |  | 1 |  |  | €0.00
 | 48 | Front and side plate |  | 1 |  |  | €0.00
 | 49 | Electronics plate |  | 1 |  |  | €0.00
 | 50 | Window |  | 1 |  |  | €0.00
 | 3D printed parts |  | Printing time | Weight (kg)
 | 51 | Clamp | 3 h, 06 min | 0.033 | €25.61 | €0.00 | €0.85
 | 52 | Clamp mount | 0 h, 56 min | 0.010 |  | €0.00 | €0.26
 | 53 | Light tower | Bottom | 0 h, 55 min | 0.008 |  | €0.00 | €0.20
 | 54 | Light tower | Spacer 1 | 0 h, 57 min | 0.009 |  | €0.00 | €0.23
 | 55 | Light tower | Spacer 2 | 1 h, 17 min | 0.012 |  | €0.00 | €0.31
 | 56 | Light tower | Top | 0 h, 26 min | 0.004 |  | €0.00 | €0.10
 | 57 | Sample stage | 2h, 19 min | 0.025 |  | €0.00 | €0.64
 | 58 | Sample stage holder | 5h, 57 min | 0.066 |  | €0.00 | €1.69
 | 59 | XY-motor mount | 1h, 32 min | 0.017 |  | €0.00 | €0.44
 | 60 | Z-motor mount | 2h, 16 min | 0.024 |  | €0.00 | €0.61
 | 61 | X-endstop mount | left | 0h, 20 min | 0.003 |  | €0.00 | €0.08
 | 62 | X-endstop mount | right | 0h, 20 min | 0.003 |  | €0.00 | €0.08
 | 63 | Y-endstop mount | front | 1h, 30 min | 0.014 |  | €0.00 | €0.36
 | 64 | Y-endstop mount | back | 1h, 23 min | 0.013 |  | €0.00 | €0.33
 | 65 | Z-endstop mount | top | 0h, 54 min | 0.008 |  | €0.00 | €0.20
 | 66 | Z-endstop mount | bottom | 0h, 54 min | 0.008 |  | €0.00 | €0.20
 | Electronics
3W and 1W | 67 | LED | 1 W | Neutral white | 1 | €0.48 | €0.00 | €0.48 |  |  | https://nl.aliexpress.com/item/32843112997.html?curPageLogUid=0nt5CjDd9UbP
 | 68 | LED heat sink |  | 1 | €1.11 | €1.21 | €2.32 |  |  | https://nl.aliexpress.com/item/32946892914.html?curPageLogUid=omekcjr4qOcD
Wrong line | 69 | Raspberry Pi HQ camera |  | 1 | €73.76 | €0.00 | €73.76 |  |  | https://nl.farnell.com/webapp/wcs/stores/servlet/AjaxOrderItemDisplayView?catalogId=15001&storeId=10168&langId=31&ddkey=https%3AOrderCalculate
Bought from farnell | 70 | Raspberry Pi Pico |  | 1 | €1.23 | €1.23 | €2.46 |  |  | https://nl.aliexpress.com/item/1005005793264636.html?_t=pvid%3A7ec7a95a-5d26-46b4-8dae-ac2173346fff
 | 71 | Male header pins | 1x20 | 2 | €0.23 | €0.00 | €0.46 |  |  | https://nl.aliexpress.com/item/1005003541838313.html?curPageLogUid=Wy3E9NlF7Oyk
 | 72 | Female header pins | 1x20 | 2 | €0.71 | €0.64 | €2.06 |  |  | https://nl.aliexpress.com/item/4001198421663.html?curPageLogUid=zlZkDgDlPU4f
 | 73 | Female header pins | 1x8 | 6 | €0.85 | €0.64 | €5.74 |  |  | https://nl.aliexpress.com/item/4001198421663.html?curPageLogUid=zlZkDgDlPU4f
 | 74 | Custom PCB |  | 1 |  |  | €0.00
 | 75 | Capacitor | 100 uF | 3 | €1.28 | €1.12 | €4.96 |  |  | https://nl.aliexpress.com/item/33049456328.html?curPageLogUid=6ku2GSQKeznm
 | 76 | MOSFET module | 15A, 400W | 1 | €0.43 | €0.91 | €1.34 |  |  | https://nl.aliexpress.com/item/32803005422.html?curPageLogUid=NExKTzmhwzbe
 | 77 | Power supply | RPD-60A | 1 | €22.63 | €0.00 | €22.63 |  |  | https://nl.farnell.com/mean-well/rpd-60a/power-supply-medical-ac-dc-2-o/dp/2815574?mckv=s_dc|pcrid|530720719616|kword|rpd%2060a|match|p|plid||slid||product||pgrid|126927693809|ptaid|kwd-382918195196|&CMP=KNC-GNL-GEN-SKU-MDC-PS_Software_TT_OE_LED-Test-985
 | 78 | Raspberry Pi 3/4 |  | 1 | €32.18 | €0.00 | €32.18 |  |  | https://nl.farnell.com/raspberry-pi/raspberrypi-modb-1gb/raspberry-pi-3-model-b/dp/2525225?src=raspberrypi
Farnelll | 79 | SD card | Silicon Power NAND | 1 | €5.49 | €0.00 | €5.49 |  |  | https://www.amazon.nl/Silicon-Power-FBE-SU032GBSTHBU1V1GEU-geheugenkaart-32/dp/B07RMXNLF4
Check Pi | 80 | Ventilator kit | for Raspberry Pi 3/4 | 1 | €4.54 | €5.66 | €10.20 |  |  | https://nl.aliexpress.com/item/1005005584107979.html?curPageLogUid=OmJkXpY4bIcm
 | 81 | TPU | Google Coral | 2 | €56.60 | €0.00 | €113.20 |  |  | https://nl.farnell.com/pi3g/g950-01456-01/usb-accelerator-raspberry-pi/dp/3583033?st=coral
 | 82 | Rocker switch | 33x25 mm | 1 | €1.12 | €0.58 | €1.70 |  |  | https://nl.aliexpress.com/item/1005001694446039.html?curPageLogUid=d1r71NCegAr7
 | 83 | Power socket | 3 pin | 1 | €0.69 | €2.69 | €3.38 |  |  | https://nl.aliexpress.com/item/4000380736505.html
 | 84 | End switch |  | 6 | €2.21 | €0.00 | €2.21 |  |  | https://nl.aliexpress.com/item/32939882024.html
 | Wires and connectors
Multiple color 5m | 85 | Wire | 22 AWG | 550 mm | 2 | €0.47 | €0.00 | €0.94 |  |  | https://nl.aliexpress.com/item/1005004750475982.html?curPageLogUid=rVN2Luqel4s8
 | 86 | Wire | 22 AWG | 400 mm | 1
 | 87 | Wire | 22 AWG | 300 mm | 4
 | 88 | Wire | 22 AWG | 250 mm | 1
 | 89 | Wire | 22 AWG | 200 mm | 4
 | 90 | Wire | 22 AWG | 120 mm | 2
 | 91 | Wire | 22 AWG | 100 mm | 1
Multiple color 5m | 92 | Wire | 10 AWG | 500 mm | 2 | €3.28 | €0.00 | €6.56 |  |  | https://nl.aliexpress.com/item/1005004750475982.html?curPageLogUid=rVN2Luqel4s8
 | 93 | Wire | 10 AWG | 350 mm | 1
 | 94 | Wire | 10 AWG | 150 mm | 2
Pins? | 95 | JST connector | XH | female | 20 | €0.91 | €0.45 | €1.36 |  |  | https://nl.aliexpress.com/item/1005004300032921.html?curPageLogUid=qhjVsdfWx3AP
Skip | 96 | JST plug | XH2P | female | 3 | €0.61 | €0.45 | €2.28 |  |  | https://nl.aliexpress.com/item/1005004300032921.html?curPageLogUid=qhjVsdfWx3AP
 | 97 | JST plug | XH4P | female | 4 | €0.83 | €0.45 | €3.77 |  |  | https://nl.aliexpress.com/item/1005004300032921.html?curPageLogUid=qhjVsdfWx3AP
 | 98 | DuPont connector | 2.54 mm | female | 2 | €0.16 | €0.93 | €1.09 |  |  | https://nl.aliexpress.com/item/4000623351046.html?curPageLogUid=rDnyKCnsIR4J
 | 99 | DuPont plug | 2.54 mm | female | 2 | €0.11 | €0.93 | €1.15 |  |  | https://nl.aliexpress.com/item/4000623351046.html?curPageLogUid=rDnyKCnsIR4J
 | 100 | RS connector set | for RPD-60A | 1 | €6.97 | €5.95 | €12.92 |  |  | https://nl.rs-online.com/web/p/power-supply-accessories/0381845
 | 101 | Spade connector | 10 AWG | 6.3 mm | 7 | €4.50 | €1.89 | €6.39 |  |  | https://nl.aliexpress.com/item/1005005743945245.html?curPageLogUid=7monaRuBNkL3
 | 102 | JST ring connector | JST FV | M3 | 1
Check | 103 | USB cable | USB-C to wire | 500 mm | 1 | €0.47 | €0.00 | €0.47 |  |  | https://nl.aliexpress.com/item/1005004982855996.html?curPageLogUid=YRx9y1l6OZRt
 | 104 | USB cable | USB to USB-C | 200 mm | 2 | €1.30 | €1.89 | €4.49 |  |  | https://nl.aliexpress.com/item/1005005064433493.html?curPageLogUid=AdH0sIMy3dcL
 | 105 | USB cable | USB to microUSB | 500 mm | 1 | €0.47 | €0.00 | €0.47 |  |  | https://nl.aliexpress.com/item/4001145014176.html?curPageLogUid=DfgWmvj4LQgR
 | 106 | USB cable | USB to microUSB | 300 mm | 1 | €0.47 | €0.00 | €0.47 |  |  | https://nl.aliexpress.com/item/4001145014176.html?curPageLogUid=DfgWmvj4LQgR
Size? Buying 300mm | 107 | USB cable | Panel mount | 2 | €1.72 | €2.15 | €5.59 |  |  | https://nl.aliexpress.com/item/1005003222744095.html
 | 108 | USB HUB | Waveshare USB HUB hat (B) | 1 | €17.52 | €1.21 | €18.73 |  |  | https://nl.aliexpress.com/item/1005005965585637.html?curPageLogUid=ohB0Wn7xGfP7
Check wrong link | 109 | HDMI cable | Panel mount | 1 | €7.05 | €6.42 | €13.47 |  |  | https://nl.aliexpress.com/item/1005001885228261.html?curPageLogUid=1yktOsx3VfsU | https://www.aliexpress.com/item/1005004082657333.html?curPageLogUid=9AYYNr9hrC1j
 | 110 | Power cable |  | 1 | €0.75 | €5.07 | €5.82 |  |  | https://nl.aliexpress.com/item/32983801295.html
 | Required tools
 |  | Soldering iron
 |  | Cable stripping tool
 |  | HEX keys | M2, M3, M4
 |  | Phillips screwdriver
 |  | Multimeter
 |  | Metal saw
 |  | Crimping tool

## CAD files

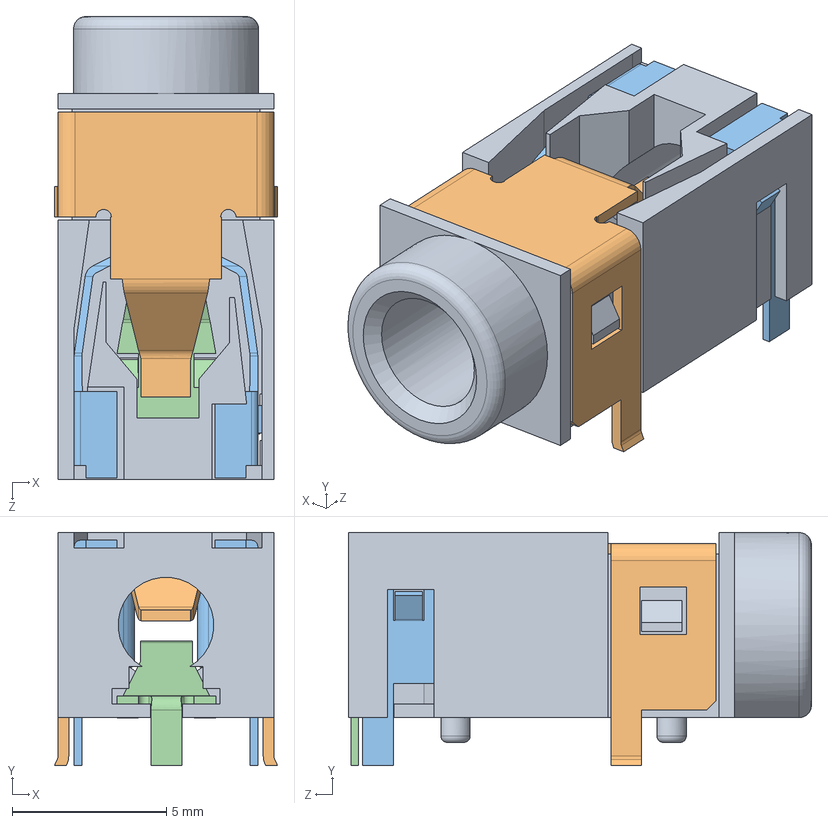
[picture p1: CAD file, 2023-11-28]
CAD/mCAD/Files for Export/Microphone plug assembly.SLDASM
7.23 x 7.55 x 15.0 mm
part 4 microphone plug
Microphone plug part 1
part 2 microphon plug metal
part 3 microphone plug

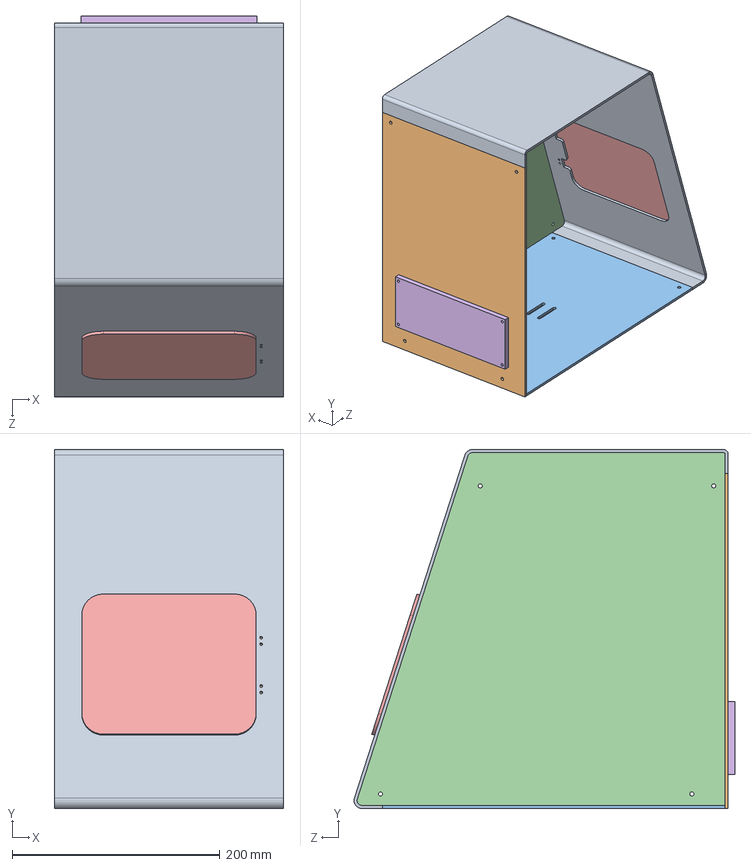
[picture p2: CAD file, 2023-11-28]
CAD/mCAD/Enclosure V2.SLDASM
221.0 x 346.0 x 367.2 mm
Top Cover
Back Panel V2
Bottom Cover V2
Side Cover V2
Door V2
IO Plate

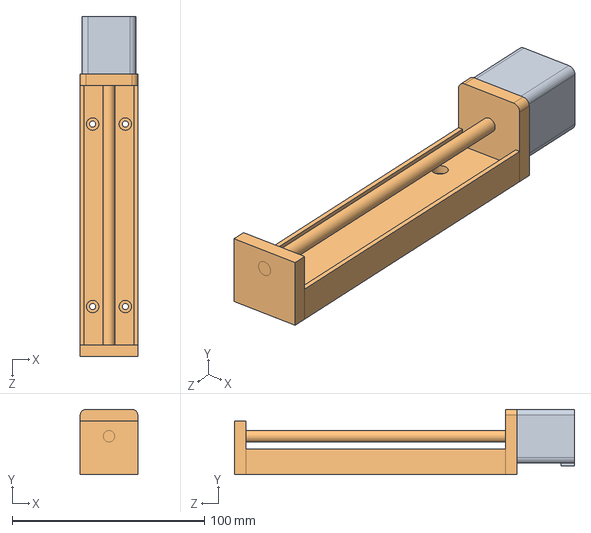
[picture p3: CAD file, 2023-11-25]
CAD/mCAD/100mm Stroke Linear Axis.SLDASM
30.0 x 34.0 x 177.0 mm
Nema 11
Gantry

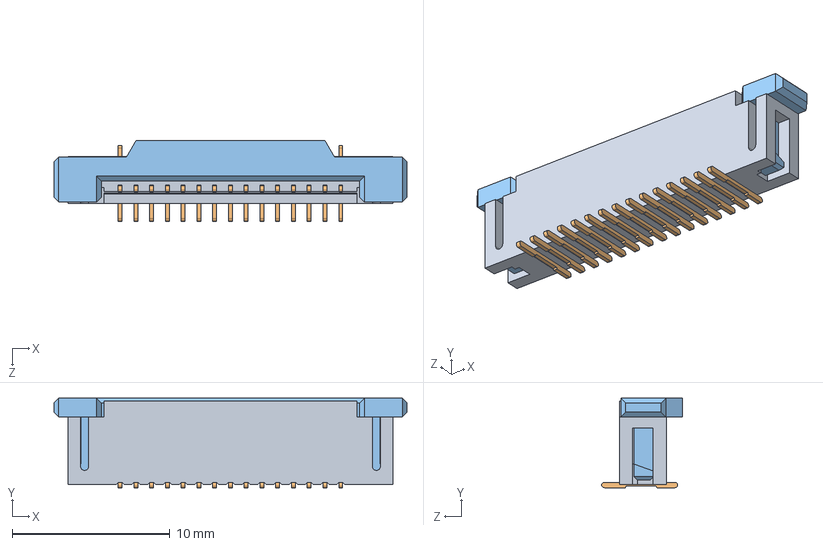
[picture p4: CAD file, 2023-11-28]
CAD/mCAD/Files for Export/Display connector assembly.SLDASM
22.4 x 5.68 x 5.12 mm
2.2 part 2 with combine
1.1 part 1 metal pin
3.3 plastic

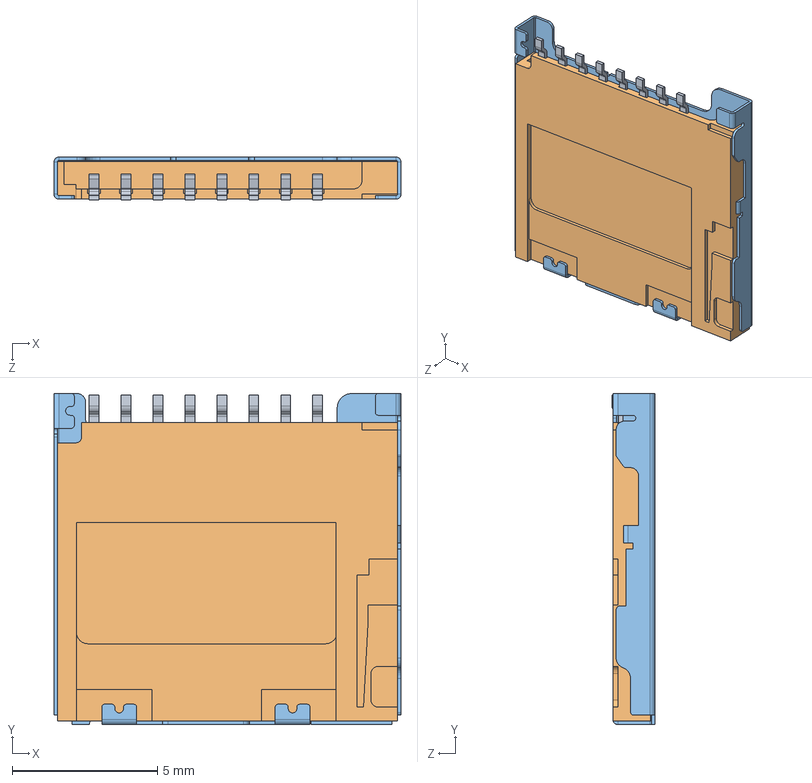
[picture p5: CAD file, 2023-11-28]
CAD/mCAD/Files for Export/Card slot assembly.SLDASM
11.9 x 11.4 x 1.48 mm
card slot part 2 metal pin
sd card slot v1
part 3 v1

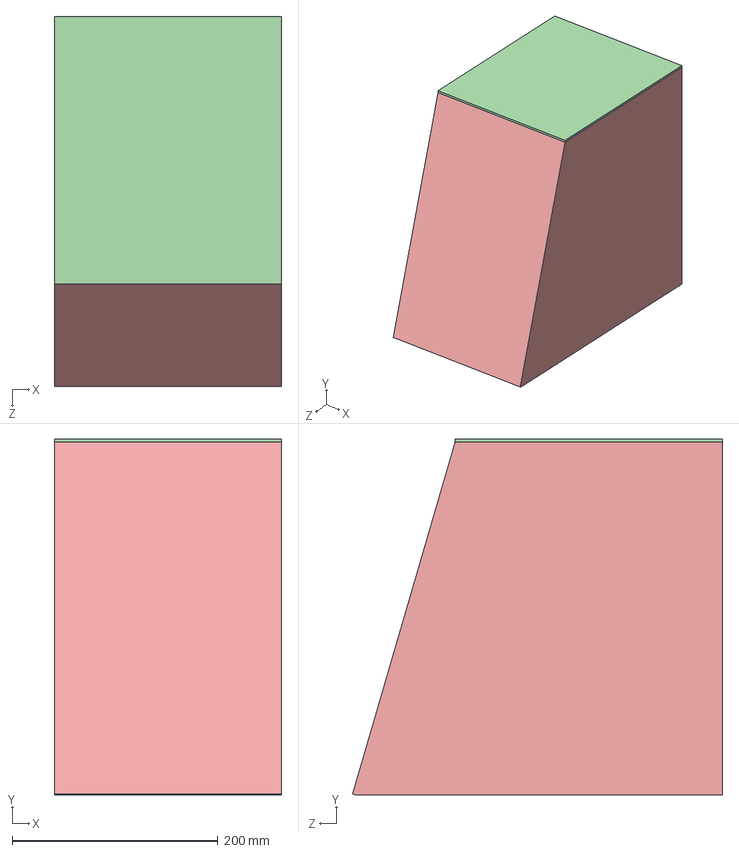
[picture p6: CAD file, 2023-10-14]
CAD/mCAD/Files for Export/Schistoscope.SLDASM
221.0 x 346.0 x 359.9 mm
aluminiumFrame
Enclosure Back Plate
Enclosure Bottom Plate
Enclosure Top Plate
Enclosure Side Plate
Electronics Mounting Plate
Right Angle Bracket x 16
socket head cap screw_iso x 62
Z Gantry Mount
Gantry
Carriage x 3
Y Gantry Base
50mm Extension Spacer
Raspberry Pi HQ Camera
Optical Tube Clamp
Objective Lens
Optical Subassembly Z Leadscrew Mount
Sample Slide

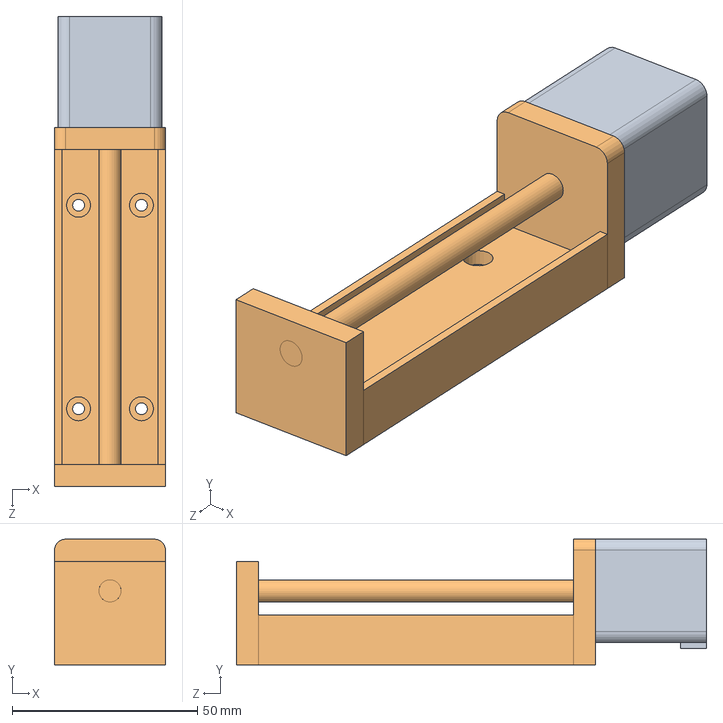
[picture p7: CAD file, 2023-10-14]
CAD/mCAD/Files for Export/50mm Stroke Linear Axis.SLDASM
30.0 x 34.0 x 127.0 mm
Nema 11
Gantry

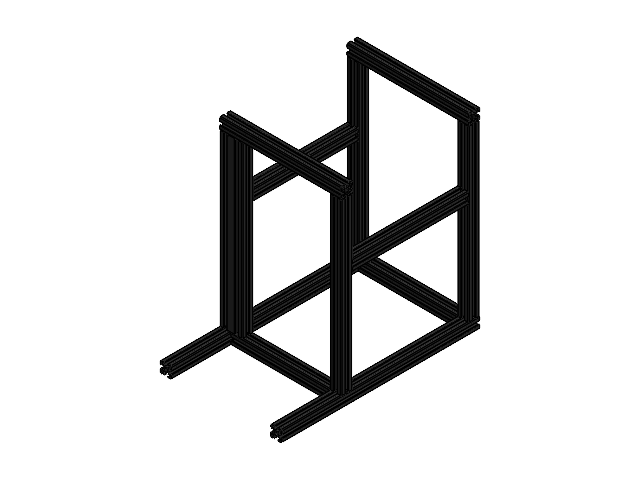
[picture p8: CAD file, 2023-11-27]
CAD/mCAD/Frame Assembly for Composer/Frame.SLDASM
20 series extrusions 20-2020(5)[2] x 2
20 series extrusions 20-2020(5)[4] x 2
20 series extrusions 20-2020(5)[7] x 3

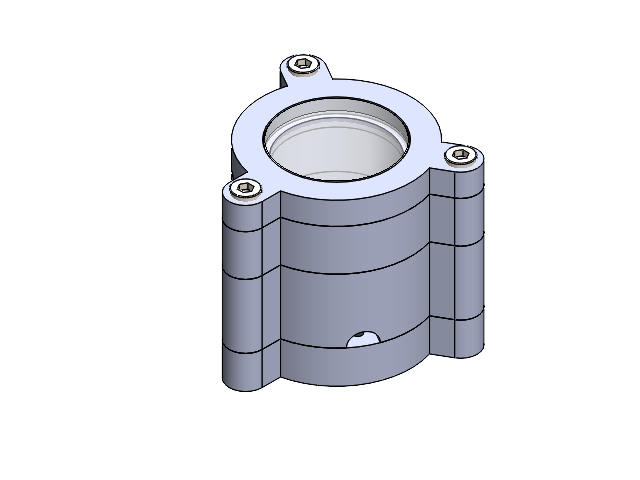
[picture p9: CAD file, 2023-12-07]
CAD/mCAD/LED Subassembly.SLDASM
Condensor Mount 1
Condensor Mount 2
Illumination Body
LED Base
Thorlabs ACL2520U-DG15
socket head cap screw_iso x 3

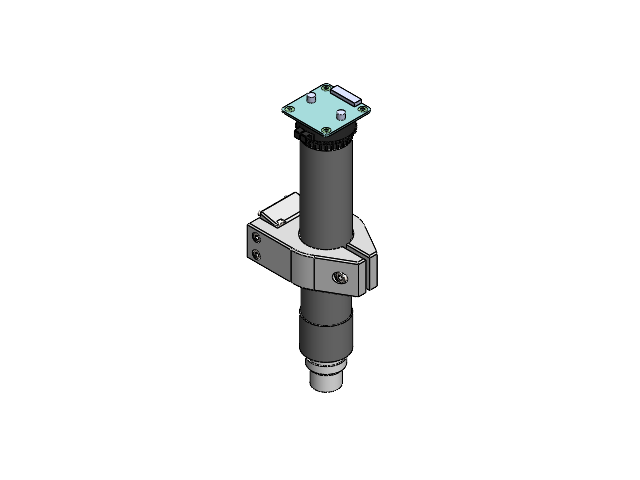
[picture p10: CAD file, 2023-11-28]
CAD/mCAD/Files for Export/Optical Subassembly.SLDASM
CML100
50mm Extension Spacer
Raspberry Pi HQ Camera
Optical Tube Clamp
Objective Lens
Optical Subassembly Z Leadscrew Mount
Heat Set Insert M3 x 4
M4 Nut
socket head cap screw_iso x 5

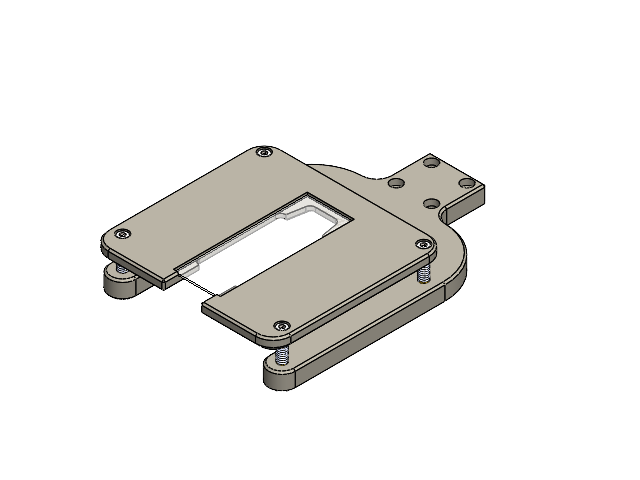
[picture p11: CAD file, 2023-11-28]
CAD/mCAD/Sample Stage Subassembly.SLDASM
Sample Stage
Sample Stage Holder
Sample Slide
Heat Set Insert M3 x 4
Sping L10 OD5 x 4
socket head cap screw_iso x 4

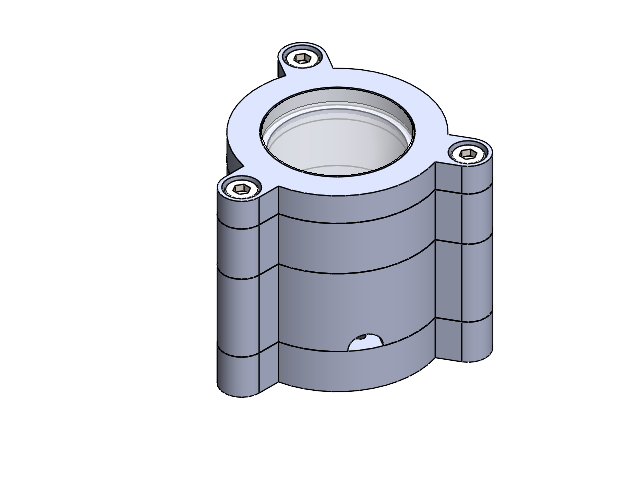
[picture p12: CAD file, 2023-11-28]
CAD/mCAD/Files for Export/LED Subassembly.SLDASM
Condensor Mount 1
Condensor Mount 2
Illumination Body
LED Base
Thorlabs ACL2520U-DG15
socket head cap screw_iso x 3

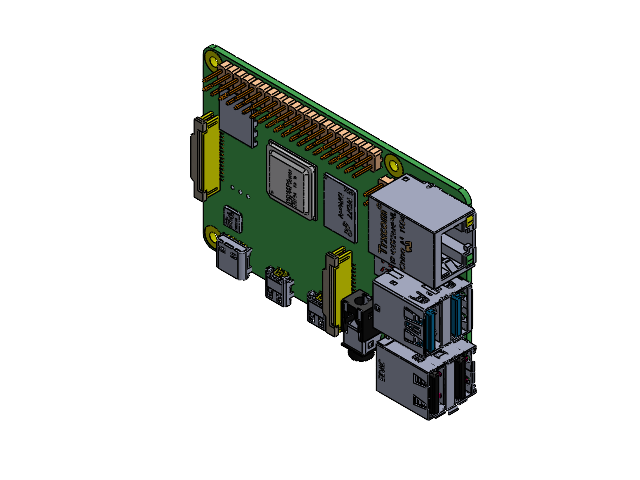
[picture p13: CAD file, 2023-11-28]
CAD/mCAD/Files for Export/Assembly Raspberry Pi 4 B.SLDASM
1.0 Plate raspberry Pi 4
2.0. PIN HEADER one
3.0 PIN HEADER 20
4.0 metal plate.
2.2 part 2 with combine x 2
1.1 part 1 metal pin x 2
3.3 plastic x 2
5.0 CPU Broadcom
6.0 9FD77 D9WHV
7.0 MxL
8.0 Gigabit Ethernet Transceiver
9.0 VLI PCIe USB 3.0 Controller
card slot part 2 metal pin
sd card slot v1
part 3 v1
11.0 Female micro HDMI connector x 2
15.0 2x USB 2.0 PORT
14.0 2x USB 3.0 PORT
10.0 Female USB connector
part 4 microphone plug
Microphone plug part 1
part 2 microphon plug metal
part 3 microphone plug
12.0 Gigabit ethernet port raspberry
9.0 VLI PCIe USB 3.0 Controller v1

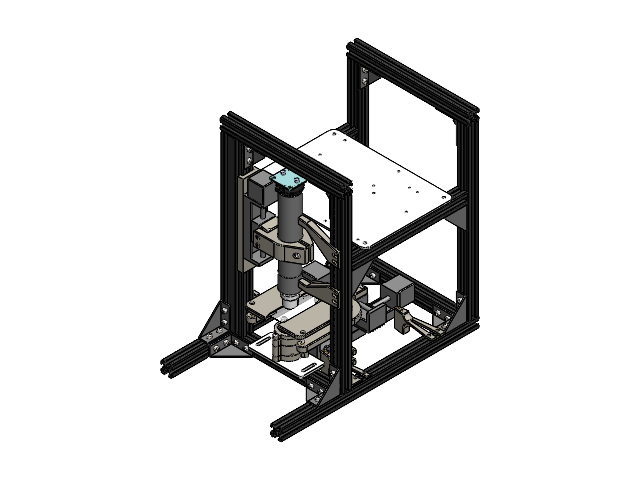
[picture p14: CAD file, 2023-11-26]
CAD/mCAD/Schistoscope.SLDASM
aluminiumFrame
Electronics Mounting Plate
Right Angle Bracket x 16
socket head cap screw_iso x 78
Z Gantry Mount
Y Gantry Base
CML100
50mm Extension Spacer
Raspberry Pi HQ Camera
Optical Tube Clamp
Objective Lens
Optical Subassembly Z Leadscrew Mount
Heat Set Insert M3 x 8
M4 Nut
Sample Stage
Sample Stage Holder
Sample Slide
countersunk flat head cross recess screw_iso x 4
50mm Stroke Gantry x 2
100mm Stroke Gantry
Y Left End Stop
Y Right End Stop
Z Bottom End Stop
Z Top End Stop
LED Mount Plate
Condensor Mount 1
Condensor Mount 2
Illumination Body
LED Base
Thorlabs ACL2520U-DG15
X Angepaast x 2
Heat Set Insert M2 x 12
Heat Set Insert M4 x 8

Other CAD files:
CAD/mCAD/Files for Export/Enclosure V2.SLDASM
CAD/mCAD/Optical Subassembly.SLDASM
CAD/mCAD/Files for Export/Sample Stage Subassembly.SLDASM
CAD/mCAD/50mm Stroke Linear Axis.SLDASM
CAD/eCAD/Schistoscope PCB/Shistoscope PCB Board.SLDPRT
CAD/mCAD/100mm Stroke Gantry.SLDPRT
CAD/mCAD/20 series extrusions 20-2020(5)[2].SLDPRT
CAD/mCAD/20 series extrusions 20-2020(5)[4].SLDPRT
CAD/mCAD/20 series extrusions 20-2020(5)[7].SLDPRT
CAD/mCAD/50mm Extension Spacer.SLDPRT
CAD/mCAD/50mm Stroke Gantry.SLDPRT
CAD/mCAD/Back Panel V2.SLDPRT
CAD/mCAD/Body3.SLDPRT
CAD/mCAD/Body5.SLDPRT
CAD/mCAD/Body6.SLDPRT
CAD/mCAD/Bottom Cover V2.SLDPRT
CAD/mCAD/Carriage.SLDPRT
CAD/mCAD/Condensor Mount 2.SLDPRT
CAD/mCAD/Door V2.SLDPRT
CAD/mCAD/Electronics Mounting Plate.SLDPRT
CAD/mCAD/Enclosure Back Plate.SLDPRT
CAD/mCAD/Enclosure Bottom Plate.SLDPRT
CAD/mCAD/Enclosure Side Plate.SLDPRT
CAD/mCAD/Enclosure Top Plate.SLDPRT
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

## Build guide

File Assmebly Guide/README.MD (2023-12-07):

# Schistoscope Assembly Maunal
## Assembly Manual



## Disclaimer

## Introduction

>The Schistoscope is a low-cost, portable microscope designed to be used in the field for the detection of schistosomiasis. This version of the Schistoscope is designed to be used with a Raspberry Pi, and is capable of imaging schistosome eggs in urine samples.

## Table of Contents

### 3D Printing Setup and Laser Cutting

### Frame Assembly

### Electronics Assembly

### X-Y Stage Assembly

### Optical Tube Assembly

### Z Stage Assembly

### Light Source Assembly

### Software Installation

### Wiring Diagram

### Enclosure Assembly

### Usage and Troubleshooting
***
-----

## 3D Printing and Setup and Laser Cutting
The scope has the following 3D printed parts:
1. Sample Stage Holder
2. Sample Stage
3. Y Gantry Base
4. Z Gantry Base
5. Y Endstop 1
6. Y Endstop 2
7. X Endstop 1
8. X Endstop 2
9.  Z Endstop 1
10. Z Endstop 2
11. Optical Tube Clamp
12. Z Lead Screw Mount
13. LED Base
14. Condesor Lens Mount 1
15. Illumination Body
16. Condensor Lens Mount 2
17. IO Plate
> It is recommeded to print the parts with the following settings:
>> 1. Layer Height: 0.2mm
>> 2. Infill: 20%
>> 3. Supports: Not Required
>> 4. Material: PETG

# Preparing the 3D Printed Parts
Some parts require additional preparation before assembly. The following parts require additional preparation:
1. Sample Stage Holder:  
Insert the M3 heat set insert into the holes (refer image) on the top of the sample stage holder. The insert should be flush with the top of the sample stage holder.  
   
1. Y Gantry Base  
Insert the M3 heat set insert into the holes (refer image) on the top of the part. The insert should be flush with the top of the part.  
   
2. Z Gantry Base  
Insert the M3 heat set insert into the holes (refer image) on the top of the part. The insert should be flush with the top of the part.  
   
3. Y Endstop 1 and Y Endstop 2
Insert the M2 heat set insert into the hole (refer image) on the top of the part. The insert should be flush with the top of the part.  
   
1. X Endstop 1 and X Endstop 2  
Insert the M2 heat set insert into the hole (refer image) on the top of the part. The insert should be flush with the top of the part.  
   
2. Z Endstop 1 and Z Endstop 2  
Insert the M2 heat set insert into the hole (refer image) on the top of the part. The insert should be flush with the top of the part.  
   
3. Z Lead Screw Mount  
Insert the M3 heat set insert into the hole (refer image) on the top of the part. The insert should be flush with the top of the part.  
   

----
The scope has the following laser cut parts:
1. Side Panel 1
2. Side Panel 2
3. Back Panel
4. Bottom Panel
5. Top Panel
6. Front Panel
7. Door
8. Light Source Base
9. Electronics Base

_____
_____

# Frame Assembly
The frame of the scope is made from 2020 (20x20mm) and 2040 (20x40mm) aluminium extrusions. The frame is secured using right angle brackets with M4x6mm screws and T-nuts.  

| Sr No. | Part | Qty |
| --- | --- | --- |
| 1 | Right Angle Bracket | 16 |
| 2 | M4x6mm Socket Head Screw | 64 |
| 3 | M4 T-nut | 64 |

The alumnum extrusion is cut to the following lengths:
###### 2020 Extrusion

| Sr No. | Length | Qty |
| --- | --- | --- |
| 1 | 350mm | 2 |
| 2 | 175mm | 2 |
| 3 | 205mm | 2 |
| 4 | 215mm | 2 |
| 5 | 300mm | 3 |

###### 2040 Extrusion

| Sr No. | Length | Qty |
| --- | --- | --- |
| 1 | 300mm | 1 |
  
The frame is assembled as follows:
1. Assemble the 2020 extrusions as shown in the image below. Hover over the table on the left to the see location of the profiles in the image on the right and vicevera.  


2. Fasten the bottom panel to the frame using M4x8mm screws (the length is depends on the your laser cut thickness) and T-nuts. 
Make sure the panel is flush with the back of the frame.  


1. Place the longest motor slide on the bottom panel as shown in the image below. Make sure the motor is at the back side. Fasten the slide to the panel using four M4 screws and hex nuts.  


1. Place the Y Gantry Base on the slide as shown in the image below. Fasten the base to the slide using four M3 screws.  


1. Place the smaller motor slide on the 3D printed part as shown in the image below. Make sure the motor is at the left side. Fasten the slide to the panel using four M4 screws.  


1. Assemble the Light Tower as shown in the image below. Just insert the M3 screws do not fasten the parts together.  


1. Place the Light Tower on the lasercut part as shown in the image below. Fasten the 3D printed parts to the panel with hex nuts and the panel using four M4 screws and T nuts.


1. Place the Z Gantry Base on the 2040 profile. Fasten the base to the profile using two M4 screws and T nuts. Then place remaining small motor slide on the base as shown in the image below. Fasten the slide to the panel using four M4 screws.  


1. Place and fasten with four M3 bolts the Z Lead Screw Mount slide as shown in the image below.  


1. Place the Thorlabs CML100 tube in the optical tube clamp as shown in the image below. Lightly fasten the tube to the clamp using one M4.  


1. Add the 50mm Extension tube to the optical tube clamp as shown in the image below.  


1. Add the objedtive lens to the tube clamp as shown in the image below.  


1. Add the Raspberry Pi Camera to the tibe top as shown in the image below.  


1. Attach the optical tube clamp to the Z Lead Screw Mount as shown in the image below. Use 4 M3 screws to fasten the clamp to the mount.  


1. Assemble the sample stage as shown in the images below.  


1. Mount the sample stage assembly on the Y Gantry Base as shown in the image below. Use 4 M3 screws to fasten them together. (The image is shown from the rear of the scope)  


1. The scope should look something like this.  


1. Mount the limit switch to the Z end stops as shown in the image below. Use 2 M2 screws to fasten them together.  
Note: the limit switch is mounted on the opposite side of the 3D printed part when mounted on the scope.  


1. Make sure that the distance between the limit switches is equal to 50mm. Try to align them to the edges of the motor slide as shown in the image below.
Adjust the motor slide, the end stop so that the objective lens does not touch the sample stage at the very bottom and the Raspberry Pi camera doesn't hit the top.  


1. Mount the limit switch to the X end stops as shown in the image below. Use 2 M2 screws to fasten them together. Follow the same procedure as the Z end stops to mount the limit switches. Repeat the procedure for the second X end stop.
Note: the limit switch is mounted on the opposite side of the 3D printed part when mounted on the scope.  


1. Make sure that the limit swtiches are mounted at the same height as sample stage.  


1. Follow the same procedure for the Y end stops. Refer the image below for more details.  


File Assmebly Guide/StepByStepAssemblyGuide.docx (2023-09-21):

1. Melt M3 Thread Inserts (4x) into the XY Motor Mount
2. Melt M3 Thread Inserts (2x) into the Light Tower | Bottom
3. Melt M3 Thread Inserts (4x) into the Sample Stage Holder
4. Melt M3 Thread Inserts (4x) into the Mounting Plate
5. Melt M2 Thread Inserts (2x) into the End Switch Mount Bottom
6. Melt M2 Thread Inserts (2x) into the End Switch Mount Top
7. Melt M2 Thread Inserts (2x) into the End Switch Mount Front
8. Melt M2 Thread Inserts (2x) into the End Switch Mount Back
9. Melt M2 Thread Inserts (2x) into the End Switch Mount Left
10. Melt M2 Thread Inserts (2x) into the End Switch Mount Right
11. Mount metal frame profiles together by means of connecting the corner brackets (16x) by means of M4x8 bolts (64x) and M4 sliding nuts (64x)
12. Connect the bottom plate by means of M4x8 bolts (4x) and M4 sliding nuts (4x)
13. Drill a hole with a diameter of 6 mm in both of the two corner brackets on the back of the device, that cover the holes in the bottom plate
14. Place the rubber legs (4x) through the bottom plate and fasten them by means of M4 nuts (8x)
15. Place the longer stepper motor on the bottom plate with the motor facing towards the back of the device, and fasten it with M3x8 bolts (4x) and M3 nuts (4x)
16. Place the XY-motor mount on the longer stepper motor and fasten it with M3x16 countersunk bolts (4x)
17. Place one of the shorter stepper motors on the XY-motor mount and fasten it with M3x8 bolts (4x)
18. Solder the LED on the heatsink, make sure that the positive and negative pins of the LED are on the allocated place
19. Strip both ends of the 22AWG | 550 mm wires (2x)
20. Solder one end of the wires on the heatsink, one on the positive pins, one on the negative pins
21. Mount the heatsink on the Light tower | Bottom by means of M3x8 bolts (2x)
22. Place Light tower | Spacer 1 on top of the Light tower | Bottom
23. Place the first of the Asymmetrical condenser lenses in the Light tower | Spacer 1
24. Place Light tower | Spacer 2 on top of Light tower | Spacer 1
25. Place the second of the Asymmetrical condenser lenses in the Light tower | Top
26. Place Light tower | Top on Light tower | Spacer 2
27. Connect all Light tower parts by means of M4x60 bolts (3x)
28. Place the Light tower assembly on the Light tower plate and fasten it with M4 nuts (3x)
29. Place the Light tower plate on the assembled structure and fasten it with M4x8 bolts (4x) and M4 sliding nuts (4x)
30. Place the Z-motor mount on the assembled structure and fasten it with M4x8 bolts (2x) and M4 sliding nuts (2x)
31. Place the other smaller stepper motor on the Z-motor mount and fasten it with M3x8 bolts (4x)
32. Place the Clamp Mount on the Smaller Stepper Motor and fasten it with M3x16 countersunk bolts (4x)
33. Place the Clamp on the Clamp Mount and fasten it with M3x12 bolts (4x)
34. Place the Thorlabs C-mount in the Clamp and tighten it with M4x24 bolts (2x) and M4 nuts (2x)
35. Screw the 50 mm Spacer on the Thorlabs C-mount
36. Screw the 4X Objective on the 50 mm Spacer
37. Screw the Raspberry Pi HQ camera on the Thorlabs C-mount
38. Place the heatsinks on the DRV8825 motor controllers (3x)
39. Solder the 1x20 Male Header Pins on the Raspberry Pi Pico (2x)
40. Upload the code to the Raspberry Pi Pico
41. Solder the 100uF capacitors on the Custom PCB
42. Solder the 1x20 Female Header Pins on the Custom PCB (2x)
43. Solder the 1x8 Female Header Pins on the Custom PCB (6x)
44. Strip both sides of the 22 AWG | 120 mm wire (2x)
45. Connect the JST XH Female Connector on one side of the wire (2x)
46. Place JST XH Female Connectors in the JST XH4P plug like depicted in the image below
47. Solder the other end of the cables to the MOSFET modules. Pay attention to polarity
48. Strip both sides of the 22 AWG | 200 mm wire (2x)
49. Connect the female Du-Pont Connector to one side of the wire (2x)
50. Slide the Du-Pont plug over the Du-Pont Connector (2x)
51. Connect the other side of the wire to the screw terminal of the MOSFET. Pay attention to the polarity.
52. Connect the USB-C to wire cable to the large connector of the RS Connector set
53. Strip both sides of the 10 AWG | 300 mm wire (2x)
54. Connect the 10 AWG | 300 mm wire to the large connector of the RS Connector set
55. Place the large connector of the RS Connector set on the RPD-60A Power supply
56. Strip both sides of the 10 AWG | 500 mm wire (2x)
57. Connect a 10 AWG | 6.3 mm Spade Connector on one side of the wire (2x)
58. Strip both sides of the 10 AWG | 350 mm wire (1x)
59. Connect a 10 AWG | 6.3 mm Spade Connector on one side of the wire (1x)
60. Connect a 10 AWG | M3 Ring Connector on the other side of the wire (1x)
61. Connect the 10 AWG | 500 mm wire to the small connector of the RS Connector set
62. Connect the small connector of the RS Connector set to the RPD-60A Power supply
63. Place a 10 mm spacer on the RPD-60A Power supply and connect it with a M2 screw (4x). Make sure to connect the M3 Ring Connector of the 10 AWG | 350 mm wire to the ground connector which is indicated by the ground symbol
64. Place the Silicon Power NAND SD Card inside the Raspberry Pi 3 or 4
65. Connect the ribbon cable to the Raspberry Pi 3 or 4, with the blue print pointing towards the USB terminals
66. Mount the fans from the Raspberry Pi Cooler set to the top part of the Raspberry Pi Cooler set
67. Stick the heat dissipation pads (3x) on the chips of the Raspberry Pi 3 or 4
68. Place the top part of the Raspberry Pi Cooler set on top of the Raspberry Pi 3 or 4
69. Connect the fan plugs to the Raspberry Pi 3 or 4
70. Connect the Custom PCB on the Electronics Plate by means of 15 mm spacers (4x), M2x8 bolts (4x) and M2 nuts (4x)
71. Connect the MOSFET on the Electronics Plate by means of 5 mm spacers (2x), M2x8 bolts (2x) and M2 nuts (2x)
72. Connect the RPD-60A Power supply on the Electronics Plate by means of M2 nuts (4x)
73. Place the bottom part of the Raspberry Pi Cooler set on the Raspberry Pi 3 or 4 and mount it to the Electronics plate by means of M2x16 mm bolts (4x)
74. Mount the Electronics Plate to the structure by means of M4x8 bolts and M4 sliding nuts (4x)
75. Mount the Sample Stage to the Sample Stage Holder by means of the M5x15 Springs (4x), M3x20 countersunk bolts (4x) and M3 rings (8x)
76. Mount the Sample Stage to Y-motor by means of M3x12 bolts (4x)
77. Connect the other side of the ribbon cable to the Raspberry Pi HQ camera, with the blue print facing upwards
78. Connect the other end of the 22AWG | 550 mm wires to the output screw terminal of the MOSFET module. Pay attention to the polarity
79. Cut and strip the cables of the Z-motor to 200 mm (4x)
80. Connect the JST XH Female Connectors to the wire (4x)
81. Place JST XH Female Connectors in the JST XH4P plug like depicted in the image below
82. Cut and strip the cables of the Y-motor to 500 mm (4x)
83. Connect the JST XH Female Connectors to the wire (4x)
84. Place the JST XH Female Connectors in the JST XH4P plug like depicted in the image below
85. Cut and strip the cables of the Y-motor to 500 mm (4x)
86. Connect the JST XH Female Connectors to the wire (4x)
87. Place the JST XH Female Connectors in the JST XH4P plug like depicted in the image below
88. Connect the JST XH4P plugs to the Custom PCB
89. Connect the Google Coral TPU to the WaveShare USB Hub Hat by means of USB-to-USB-C cables | 200 mm (2x)
90. Mount the Google Coral TPU (2x) to the structure by means of M3x12 bolts (2x) and M3 sliding nuts (2x)
91. Mount the WaveShare USB Hub Hat to the structure by means of the 3D printed spacers (2x), M3x16 bolts (2x) and M3 sliding nuts (2x)
92. Mount the WaveShare USB Hub Hat to the Raspberry Pi 3 or 4 by means of a USB-to-microUSB cable | 500 mm
93. Mount the USB Panel Mount Cables (2x) to the Mounting Plate by means of M3x8 bolts (4x)
94. Mount the Rocker Switch to the Mounting Plate
95. Mount the Power Socket to the Mounting Plate by means of M3x16 bolts (2x) and M3 nuts (2x)
96. Mount the HDMI Panel Mount Cable to the Mounting Plate by means of M3x6 bolts (2x)
97. Mount the Mounting Plate to the Backplate by means of M3x12 bolts (4x) and M3 nuts (4x)
98. Strip both sides of the 10 AWG | 150 mm wires (2x)
99. Connect 10 AWG | 6.3 mm Spade Connectors to both sides of the wires (4x)
100. Mount the Backplate to the structure by means of M4x8 bolts (4x) and M4 sliding nuts (4x)
101. Connect the USB panel mount cables to the Raspberry Pi 3 or 4
102. Connect the HDMI panel mount cable to the Raspberry Pi 3 or 4
103. Connect the spade connectors of the 10 AWG | 150 mm wires to the Power Socket and the Rocker Switch
104. Connect the spade connector of the 10 AWG | 350 mm wire to the Power Socket
105. Connect the spade connectors of the 10 AWG | 500 mm wires to the Rocker Switch
106. Connect the Raspberry Pi Pico to the Raspberry Pi 3 or 4 by means of the USB-to-microUSB | 300 mm
107. Strip both sides of the 22 AWG | 100 mm (1x), 22 AWG | 200 mm (1x) and 22 AWG | 250 mm (1x) wires
108. Solder the 22 AWG | 100 mm, 22 AWG | 200 mm and 22 AWG | 250 mm wires to the End Switches (2x) as depicted in the figure below
109. Connect the JST XH Female Connectors to the wire (2x)
110. Place JST XH Female Connectors in the JST XH2P plug like depicted in the image below
111. Mount the End Switches to the End Switch Mount Top and End Switch Mount Bottom by means of M2x10 bolts (4x)
112. Mount the End Switch Mount Top and End Switch Mount Bottom to the structure by means of M4x8 bolts (4x) and M4 sliding nuts (4x)
113. Align the End Switch Mount Top in such a way that the Raspberry Pi HQ Camera cannot hit the aluminium profiles at the top
114. Align the End Switch Mount Bottom in such a way that the objective cannot hit the glass sample slide on the stage
115. Connect the JST XH2P plug to Custom PCB
116. Strip both sides of the 22 AWG | 200 mm (1x), 22 AWG | 300 mm (1x) and 22 AWG | 400 mm (1x) wires
117. Solder the 22 AWG | 200 mm, 22 AWG | 300 mm and 22 AWG | 400 mm wires to the End Switches (2x) as depicted in the figure below
118. Connect the JST XH Female Connectors to the wire (2x)
119. Place JST XH Female Connectors in the JST XH2P plug like depicted in the image below
120. Mount the End Switches to the End Switch Mount Front and End Switch Mount Back by means of M2x10 bolts (4x)
121. Mount the End Switch Mount Front and End Switch Mount Back to the structure by means of M4x12 bolts (4x) and M4 sliding nuts (4x)
122. Align the End Switch Mount Front in such a way, so that it hits the aluminium profile
123. Align the End Switch Mount Back in such a way, so that it hits the aluminium profile
124. Connect the JST XH2P plug to Custom PCB
125. Strip both sides of the 22 AWG | 300 mm (1x), 22 AWG | 300 mm (1x) and 22 AWG | 300 mm (1x) wires
126. Solder the 22 AWG | 300 mm, 22 AWG | 300 mm and 22 AWG | 300 mm wires to the End Switches (2x) as depicted in the figure below
127. Connect the JST XH Female Connectors to the wire (2x)
128. Place JST XH Female Connectors in the JST XH2P plug like depicted in the image below
129. Mount the End Switches to the End Switch Mount Left and End Switch Mount Right by means of M2x10 bolts (4x)
130. Mount the End Switch Mount Left and End Switch Mount Right to the structure by means of M4x12 bolts (4x) and M4 sliding nuts (4x)
131. Align the End Switch Mount Left so that the Sample Stage cannot hit the Light tower
132. Align the End Switch Mount Right so that the Sample Stage cannot hit the Light tower
133. Connect the JST XH2P plug to Custom PCB
134. Mount the Top Plate on the structure by means of M4x8 bolts (4x) and M4 sliding nuts (4x)
135. Place the hinges (2x) on the Side Plate by means of M2x8 bolts (4x) and M2 nuts (4x)
136. Mount the Lock Mount on the Side Plate by means of M2x8 bolts (2x) and M2 nuts (2x)
137. Mount the Lock Hook on the Window by means of a M3x8 bolt (1x), a M3 nut (1x) and a M3 ring (1x)
138. Mount the Window to the Side Plate by means of M2x6 bolts (4x) and M2 nuts (4x)
139. Mount the Side Plate to the structure by means of M4x8 bolts (10x) and M4 sliding nuts (10x)
140. Connect the Power Cord to the Power Plug and connect it to the grid
141. Connect the Schistoscope to a monitor by means of an HDMI cable
142. Move the Light Tower plate until it is aligned perfectly with the objective as can be observed on the monitor
143. Set the DRV8825 Stepper Motor Controllers’ reference voltage (Vref) to 0.6V

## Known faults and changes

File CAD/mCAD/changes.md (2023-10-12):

1. Made the mid section slightly wider 205 vs. 200 to make the back flat
2. Modified C-Clamp to have less screws
3. Modified Sample Stage Holder to better accomodate X axis movement
4. Modified Sample Stage due to complexity of getting accurate dimensions

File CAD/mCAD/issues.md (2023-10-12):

1. Condenser tube (CML100) clamp has 3 differnt types of screws.
2. Wiring is messy
3. Different length screws for the back plate.

-- Moved to Issues in Github

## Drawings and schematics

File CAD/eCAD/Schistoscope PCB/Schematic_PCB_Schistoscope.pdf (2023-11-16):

# A212 GND15

# A212 GND15

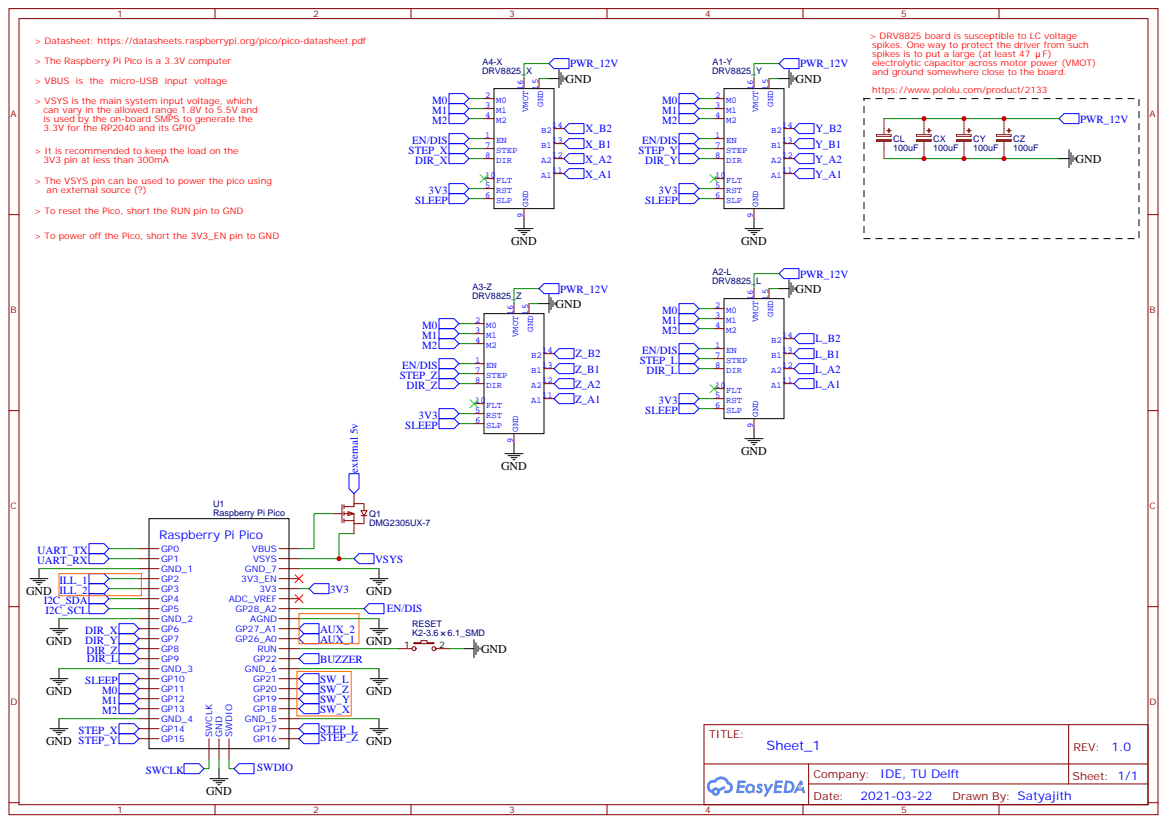
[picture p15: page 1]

> DRV8825 board is susceptible to LC voltage
spikes. One way to protect the driver from such
spikes is to put a large (at least 47 F)
electrolytic capacitor across motor power (VMOT)
and ground somewhere close to the board.
https://www.pololu.com/product/2133

> Datasheet: https://datasheets.raspberrypi.org/pico/pico-datasheet.pdf
> The Raspberry Pi Pico is a 3.3V computer
> VBUS is the micro-USB input voltage
> VSYS is the main system input voltage, which
can vary in the allowed range 1.8V to 5.5V and
is used by the on-board SMPS to generate the
3.3V for the RP2040 and its GPIO

> It is recommended to keep the load on the
3V3 pin at less than 300mA

> The VSYS pin can be used to power the pico using
an external source (?)

> To reset the Pico, short the RUN pin to GND

> To power off the Pico, short the 3V3_EN pin to GND

Company: IDE, TU Delft

# Endswitches

# Peripherals

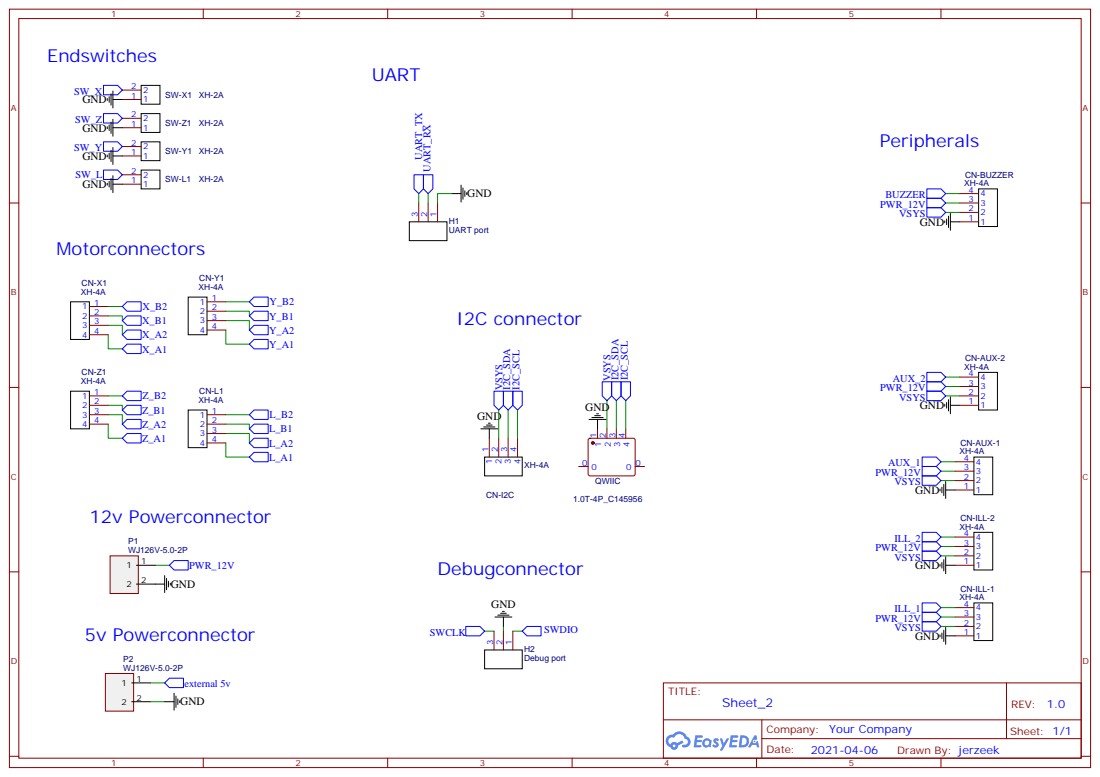
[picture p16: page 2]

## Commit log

2023-09-21 Added the BOM and Assembly files from Patrick
    [BillOfMaterials.xlsx]
2023-09-21 Started to split
    [BillOfMaterials.xlsx]
2023-09-28 Started CAD and basic frames
    [BillOfMaterials.xlsx, aluminiumFrame.SLDPRT]
2023-10-05 Frame + Fasteners
    [Electronics Mounting Plate.SLDPRT, Enclosure Back Plate.SLDPRT, Enclosure Bottom Plate.SLDPRT, Enclosure Side Plate.SLDPRT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]
2023-10-05 Updated Frame + Fasteners
    Having issues with smart fasteners feature
    [BillOfMaterials.xlsx, Schistoscope.SLDASM]
2023-10-05 Updated Frame + Fasteners | Found issue with BOM
    BOM calls for CML50, but I noticed that the scope uses CML100(!)
    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
    [BillOfMaterials.xlsx, Schistoscope.SLDASM]
2023-10-06 Pack and Go
    [Electronics Mounting Plate.SLDPRT, Enclosure Back Plate.SLDPRT, Enclosure Bottom Plate.SLDPRT, Enclosure Side Plate.SLDPRT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]
2023-10-06 Exported Pack and Go to STEP
    [Schistoscope.SLDASM]
2023-10-09 Updated Assem
    [Schistoscope.SLDASM]
2023-10-09 Added Optical Subassembly
    Modified the RaspiHQ Camera file from https://grabcad.com/library/hq-cam-v-1-0-1
    [50mm Extension Spacer.SLDPRT, Objective Lens.SLDPRT, Optical Subassembly.SLDASM, Optical Tube Clamp.SLDPRT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]
2023-10-12 Updated Optical Subassembly
    [Optical Subassembly Z Leadscrew Mount.SLDPRT, Optical Subassembly.SLDASM, Optical Tube Clamp.SLDPRT]
2023-10-12 Sample Stage New
    [Sample Stage Holder v2.SLDPRT, Sample Stage.SLDPRT]
2023-10-12 File rename
    [Sample Stage Holder.SLDPRT]
2023-10-12 Sample Stage Subassembly
    [Sample Stage Holder.SLDPRT, Sample Stage Subassembly.SLDASM, Sample Stage.SLDPRT]
2023-10-13 Fixed Gantry Configurations
    [100mm Stroke Linear Axis.SLDASM, 50mm Stroke Linear Axis.SLDASM, Gantry 50mm.SLDASM, Gantry.SLDPRT]
2023-10-13 3D printed Mounts
    [Schistoscope.SLDASM, Z Gantry Mount.SLDPRT]
2023-10-14 Added Optical and sample stage in the Assembly
    [50mm Stroke Linear Axis.SLDASM, Schistoscope.SLDASM, Y Gantry Base.SLDPRT, Z Gantry Mount.SLDPRT]
2023-10-14 Pack and Go
    Pack and Go for milestone
    [100mm Stroke Linear Axis.SLDASM, 50mm Extension Spacer.SLDPRT, 50mm Stroke Linear Axis.SLDASM, Carriage.SLDPRT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]
2023-10-14 Trying to make the clamp more printable
    [Optical Subassembly Z Leadscrew Mount.SLDPRT, Optical Subassembly.SLDASM, Optical Tube Clamp.SLDPRT, Sping L15 OD5.SLDPRT]
2023-10-24 LED Base
    [50mm Stroke Linear Axis.SLDASM, LED Base.SLDPRT, Schistoscope.SLDASM]
2023-10-24 Condenser Mount 1
    [Condensor Mount 1.SLDPRT]
2023-10-24 Condenser Mount 2 - Top Seal
    [Condensor Mount 2.SLDPRT]
2023-10-24 End Stop Y Left
    [Y Left End Stop.SLDPRT]
2023-10-25 Chamfers to Y end stop
    [Y Left End Stop.SLDPRT]
2023-10-25 Y End Stop Right
    [Y Right End Stop.SLDPRT]
2023-10-25 Illumination Body
    [Illumination Body.SLDPRT]
2023-10-25 X Angepaast
    [X Angepaast.SLDPRT]
2023-10-27 Adds outlines pcb
    [pcb.step]
2023-10-31 Edited Folder Structure
    [100mm Stroke Linear Axis.SLDASM, 50mm Extension Spacer.SLDPRT, 50mm Stroke Linear Axis.SLDASM, Carriage.SLDPRT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]
2023-10-31 Fixed Optical Sub assembly
    [Optical Subassembly Z Leadscrew Mount.SLDPRT, Optical Subassembly.SLDASM, Optical Tube Clamp.SLDPRT]
2023-10-31 Fixing Missing Items (Z End Stops)
    [Z Bottom End Stop.SLDPRT, Z Top End Stop.SLDPRT]
2023-10-31 IO Plate (Missing)
    Need to fix the holes for power and USB
    [IO Plate.SLDPRT]
2023-10-31 LED Mount Plate (Missing)
    [LED Mount Plate.SLDPRT]
2023-10-31 Add Rasp Pi4
    https://grabcad.com/library/raspberry-pi-4-model-b-3
    [Raspberry Pi 4B.SLDPRT]
2023-11-07 Modified the file to fit the purchased M2 inserts
    [Y Right End Stop.SLDPRT, Z Bottom End Stop.SLDPRT, Z Top End Stop.SLDPRT]
2023-11-07 Modified the file to fit the purchased M2/M3 inserts
    [Sample Stage Holder.SLDPRT, Y Right End Stop.SLDPRT, Z Bottom End Stop.SLDPRT, Z Top End Stop.SLDPRT]
2023-11-07 Added Longer clamp to the official build
    [Optical Tube ClampV2.SLDPRT]
2023-11-07 Minor Updates
    [50mm Stroke Linear Axis.SLDASM, BillOfMaterials.xlsx, Optical Subassembly Z Leadscrew Mount.SLDPRT, Optical Subassembly.SLDASM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]
2023-11-07 Modified according to Inserts
    [X Angepaast.SLDPRT]
2023-11-08 Updated Dimensions
    [Sample Stage Holder.SLDPRT]
2023-11-13 Updated/Fixed Hole misalignment Z Axis
    [50mm Stroke Linear Axis.SLDASM, Carriage.SLDPRT, Optical Subassembly Z Leadscrew Mount.SLDPRT, Optical Subassembly.SLDASM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]
2023-11-13 Fixed Dimensions issues
    [Condensor Mount 2.SLDPRT, LED Subassembly.SLDASM]
2023-11-13 Fixed graphic glitch
    No edits to the file
    [Illumination Body.SLDPRT]
2023-11-13 Updated Hole Dimensions
    [Electronics Mounting Plate.SLDPRT]
2023-11-13 New Enclosure
    [Back Panel V2.SLDPRT, Bottom Cover V2.SLDPRT, Door V2.SLDPRT, Enclosure V2.SLDASM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]
2023-11-13 General Assembly Updates
    [50mm Stroke Linear Axis.SLDASM, Optical Subassembly.SLDASM, Sample Stage Holder.SLDPRT, Sample Stage Subassembly.SLDASM]
2023-11-13 Assmebly Updates
    [50mm Stroke Linear Axis.SLDASM, Enclosure V2.SLDASM, Schistoscope.SLDASM]
2023-11-18 Auto stash before merge of "master" and "origin/master"
    [50mm Stroke Linear Axis.SLDASM, Bottom Cover V2.SLDPRT, Door V2.SLDPRT, Enclosure V2.SLDASM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]
2023-11-25 Fixed Dimension again
    [Sample Stage Holder.SLDPRT]
2023-11-25 Updated colours and textures
    Preparing for rendering / composer
    [100mm Stroke Linear Axis.SLDASM, 50mm Extension Spacer.SLDPRT, 50mm Stroke Linear Axis.SLDASM, Back Panel V2.SLDPRT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]
2023-11-25 Started Composer Documentation Update
    [Electronics Mounting Plate.SLDPRT, Enclosure Bottom Plate.SLDPRT, Enclosure Side Plate.SLDPRT, Heat Set Insert M3.SLDPRT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]
2023-11-26 Tidy up for composer
    [100mm Stroke Gantry.SLDPRT, 50mm Stroke Gantry.SLDPRT, Electronics Mounting Plate.SLDPRT, Enclosure Bottom Plate.SLDPRT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]
2023-11-26 Final Touches
    [Condensor Mount 1.SLDPRT, Condensor Mount 2.SLDPRT, Illumination Body.SLDPRT, LED Base.SLDPRT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]
2023-11-26 Heat Set Inserts
    [Heat Set Insert M2.SLDPRT, Heat Set Insert M4.SLDPRT, LED Subassembly.SLDASM, Sample Stage Subassembly.SLDASM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]
2023-11-26 Added accurate Pi4B Model
    https://grabcad.com/library/raspberry-pi-4-model-b-5
    [1.0 Plate raspberry Pi 4.SLDPRT, 1.1 part 1 metal pin.SLDPRT, 10.0 Female USB connector.SLDPRT, 11.0 Female micro HDMI connector.SLDPRT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]
2023-11-26 Updated the Model to fit the Rpi properly
    [1.0 Plate raspberry Pi 4.SLDPRT, 1.1 part 1 metal pin.SLDPRT, 10.0 Female USB connector.SLDPRT, 11.0 Female micro HDMI connector.SLDPRT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]
2023-11-26 Limit Switches
    Also removed the inaccurate rpi model
    [Limit Switch.SLDPRT, Raspberry Pi 4B.SLDPRT, Sample Stage Subassembly.SLDASM]
2023-11-26 Change Spring Dims
    [Sample Stage Subassembly.SLDASM, Sping L10 OD5.SLDPRT, Sping L15 OD5.SLDPRT]
2023-11-26 Added Power Supply Files and cleaned up eCad Folder
    [Meanwell RPD-60.SLDPRT, Shistoscope PCB Board.SLDPRT, pcb.step]
2023-11-26 Pack n Go for Export and Added Electronics
    [1.0 Plate raspberry Pi 4.SLDPRT, 1.1 part 1 metal pin.SLDPRT, 10.0 Female USB connector.SLDPRT, 100mm Stroke Gantry.SLDPRT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]
2023-11-26 Added Springs
    [Sample Slide.SLDPRT, Sample Stage Holder.SLDPRT, Sample Stage Subassembly.SLDASM, Sample Stage.SLDPRT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]
2023-11-27 Start Documentation
    [Sample Stage Subassembly.SLDASM]
2023-11-27 Fire alarm
    [20 series extrusions 20-2020(5)[2].SLDPRT, 20 series extrusions 20-2020(5)[4].SLDPRT, 20 series extrusions 20-2020(5)[7].SLDPRT, Body3.SLDPRT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]
2023-11-28 Fixed Screw size mismatch in the XY GAntry
    [100mm Stroke Gantry.SLDPRT, 50mm Stroke Gantry.SLDPRT, Bottom Cover V2.SLDPRT, Enclosure V2.SLDASM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]
2023-11-28 M4 --> M3 heat set insert
2023-11-28 Updated to new dimensions
    [IO Plate.SLDPRT]
2023-11-28 Composer edits
    [Enclosure V2.SLDASM, Sample Stage Subassembly.SLDASM, Z Gantry Mount.SLDPRT]
2023-11-28 Assembly Documentation
    [100mm Stroke Gantry.SLDPRT, 2.2 part 2 with combine.SLDPRT, 20 series extrusions 20-2020(5)[2].sldprt, 20 series extrusions 20-2020(5)[4].sldprt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]
2023-11-28 Mech Assembly Sorted
2024-06-24 Create wiring diagram
